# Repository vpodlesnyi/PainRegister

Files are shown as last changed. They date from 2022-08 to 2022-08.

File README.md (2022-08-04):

# PainRegister
The PCB of an electrostimulator for the study of the method of objective pain registration.

Technical specifications:
- input voltage supply 5V;
- booster scheme on the UC3843BD1013TR;
- USB-UART module;
- main MCU STM32F103C8T6TR.

demo image

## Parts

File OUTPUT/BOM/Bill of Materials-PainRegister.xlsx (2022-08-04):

Description | Part Number | Value | Voltage | Designator | Quantity
DC-DC step-up converter for 5/32-V to 5/35-V |  |  |  | A1 | 1
USB UART module |  |  |  | A2 | 1
Конденсатор | GRM216R71H103K | 0,01мк | 50B | C1 | 1
Конденсатор | GRM21BR71H104KA01L | 0,1мк | 50В | C2, C3, C5, C9, C19, C21, C38 | 7
Конденсатор | GRM21BR71H105K | 1мк | 50B | C4, C6, C37 | 3
Конденсатор полярный | TAJD336K035RNJ | 33мк | 35В | C7 | 1
Конденсатор полярный | 293D106X9016A2TE3 | 10мк | 16В | C8, C22, C24, C25, C26, C36 | 6
Конденсатор | GRM188R71H104KA93D | 0,1мк | 50B | C10, C11, C13, C14, C15, C16 | 6
Конденсатор | CC0603JRNPO9BN220 | 22 | 50B | C12, C17 | 2
Конденсатор | GRM31CR71E106KA12L* | 10мк | 25В | C18 | 1
Конденсатор | GRM21BR61E475KA12L | 4,7мк | 25B | C23, C33 | 2
Конденсатор | GRM32ER71H106K | 10мк | 50В | C27 | 1
Конденсатор | GRM1885C1H151J | 150 | 50B | C28 | 1
Конденсатор | GRM319R71H223K | 0,022мк | 50В | C29 | 1
Конденсатор полярный | ECAP33uF/450V | 33мк | 450В | C30 | 1
Конденсатор | GRM1885C1H101J | 100 | 50B | C31 | 1
Конденсатор | GRM216R71H222K | 2200 | 50В | C34 | 1
Конденсатор | CC1206JRNPOBBN101 | 100 | 500В | C35 | 1
Low Cost Low Power Instrumentation Amplifier | INA122PU |  |  | DA1 | 1
4-Bit Bidirectional Voltage-level Translator | TXB0104PWR |  |  | DA2 | 1
Step-Down DC-DC Converter | LM3671MF-3.3/NOPB |  |  | DA3 | 1
High and Low Side Driver | IR2110STRPBF |  |  | DA4 | 1
Current Mode PWM Controller for Forward and Flyback Applications | UC3843BD1013TR |  |  | DA5 | 1
Medium-density performance line ARM®-based 32-bit MCU with 64 or 128 KB Flash, USB, CAN, 7 timers, 2 ADCs, 9 com. interfaces | STM32F103C8T6TR |  |  | DD1 | 1
Предохранитель | MF-MSMF260 |  |  | FU1 | 1
EMI Suppression Filter | BLM18PG181SN1D | 0 |  | L1 | 1
EMI Suppression Filter | SRR0604-3R3ML | 3,3мкГн |  | L2, L4, L6, L8 | 4
EMI Suppression Filter | CM201212-R18KL | 0,18мкГн |  | L3, L5, L9 | 3
EMI Suppression Filter | SRP1770TA-101M | 100мкГн |  | L7 | 1
Резистор | RC0805FR-07100RL | 100 |  | R1 | 1
Potentiometer | 3296Y-1-202LF | 2к |  | R2 | 1
Резистор | RC0805FR-07510RL | 510 |  | R3 | 1
Резистор | RC0805FR-0747RL | 47 |  | R4, R21 | 2
Резистор | RC1206FR-074M3 | 4,3М |  | R5 | 1
Резистор | RC0805FR-071KL | 1к |  | R6, R19, R24 | 3
Резистор | RC0805FR-0710RL | 10 |  | R7, R26 | 2
Резистор | RC0805FR-0747KL | 47к |  | R8, R11, R25 | 3
Резистор | RC0603FR-0710KL | 10к |  | R9, R10 | 2
Резистор | RC1206FR-071M2 | 1,2М |  | R12 | 1
Резистор | RC0805FR-0710KL | 10к |  | R13, R23 | 2
Резистор | RC0805FR-070RL | 0 |  | R14, R15 | 2
Резистор | RC0805FR-077K5 | 7,5к |  | R16 | 1
Резистор | RC1206FR-07100RL | 100 |  | R17 | 1
Potentiometer | 3296Y-1-203LF | 20к |  | R18 | 1
Резистор | RC0805FR-07150RL | 150 |  | R20 | 1
Резистор | KNP-2W-1KJ | 1 |  | R22 | 1
Резистор | RC1206FR-07150RL | 150 |  | R27 | 1
Резистор | RC0805FR-0791RL | 91 |  | R28 | 1
Резистор | RC2512FR-07330RL | 330 |  | R29 | 1
Кнопка |  |  |  | S1 | 1
Диод | SMA4007 |  |  | VD1, VD8 | 2
Диод Шоттки | PMEG2010AEB.115 |  |  | VD2, VD7 | 2
Диод | GS1M |  |  | VD3 | 1
Cтабилитрон (лавинный выпрямительный диод) односторонний | SMAJ5.0A |  |  | VD4 | 1
Диод Шоттки | MBR0520LT1 |  |  | VD5, VD9 | 2
Диод Шоттки | SK34A |  |  | VD6 | 1
Светодиод | KP-2012EC |  |  | VD10, VD11 | 2
N-MOSFET | IRLML6401TRPBF |  |  | VT1 | 1
N-MOSFET | IRF840ASPBF |  |  | VT2, VT3, VT4 | 3
Разъем - 6 конт. вилка | DS1021-1*6SF112-B |  |  | X1 | 1
Разъем - 2 конт. розетка | DS1069-2 MR-A |  |  | X2 | 1
Разъем - 2 конт. клеммник |  |  |  | X3 | 1
Кварцевый резонатор | KX-9A |  |  | Z1 | 1

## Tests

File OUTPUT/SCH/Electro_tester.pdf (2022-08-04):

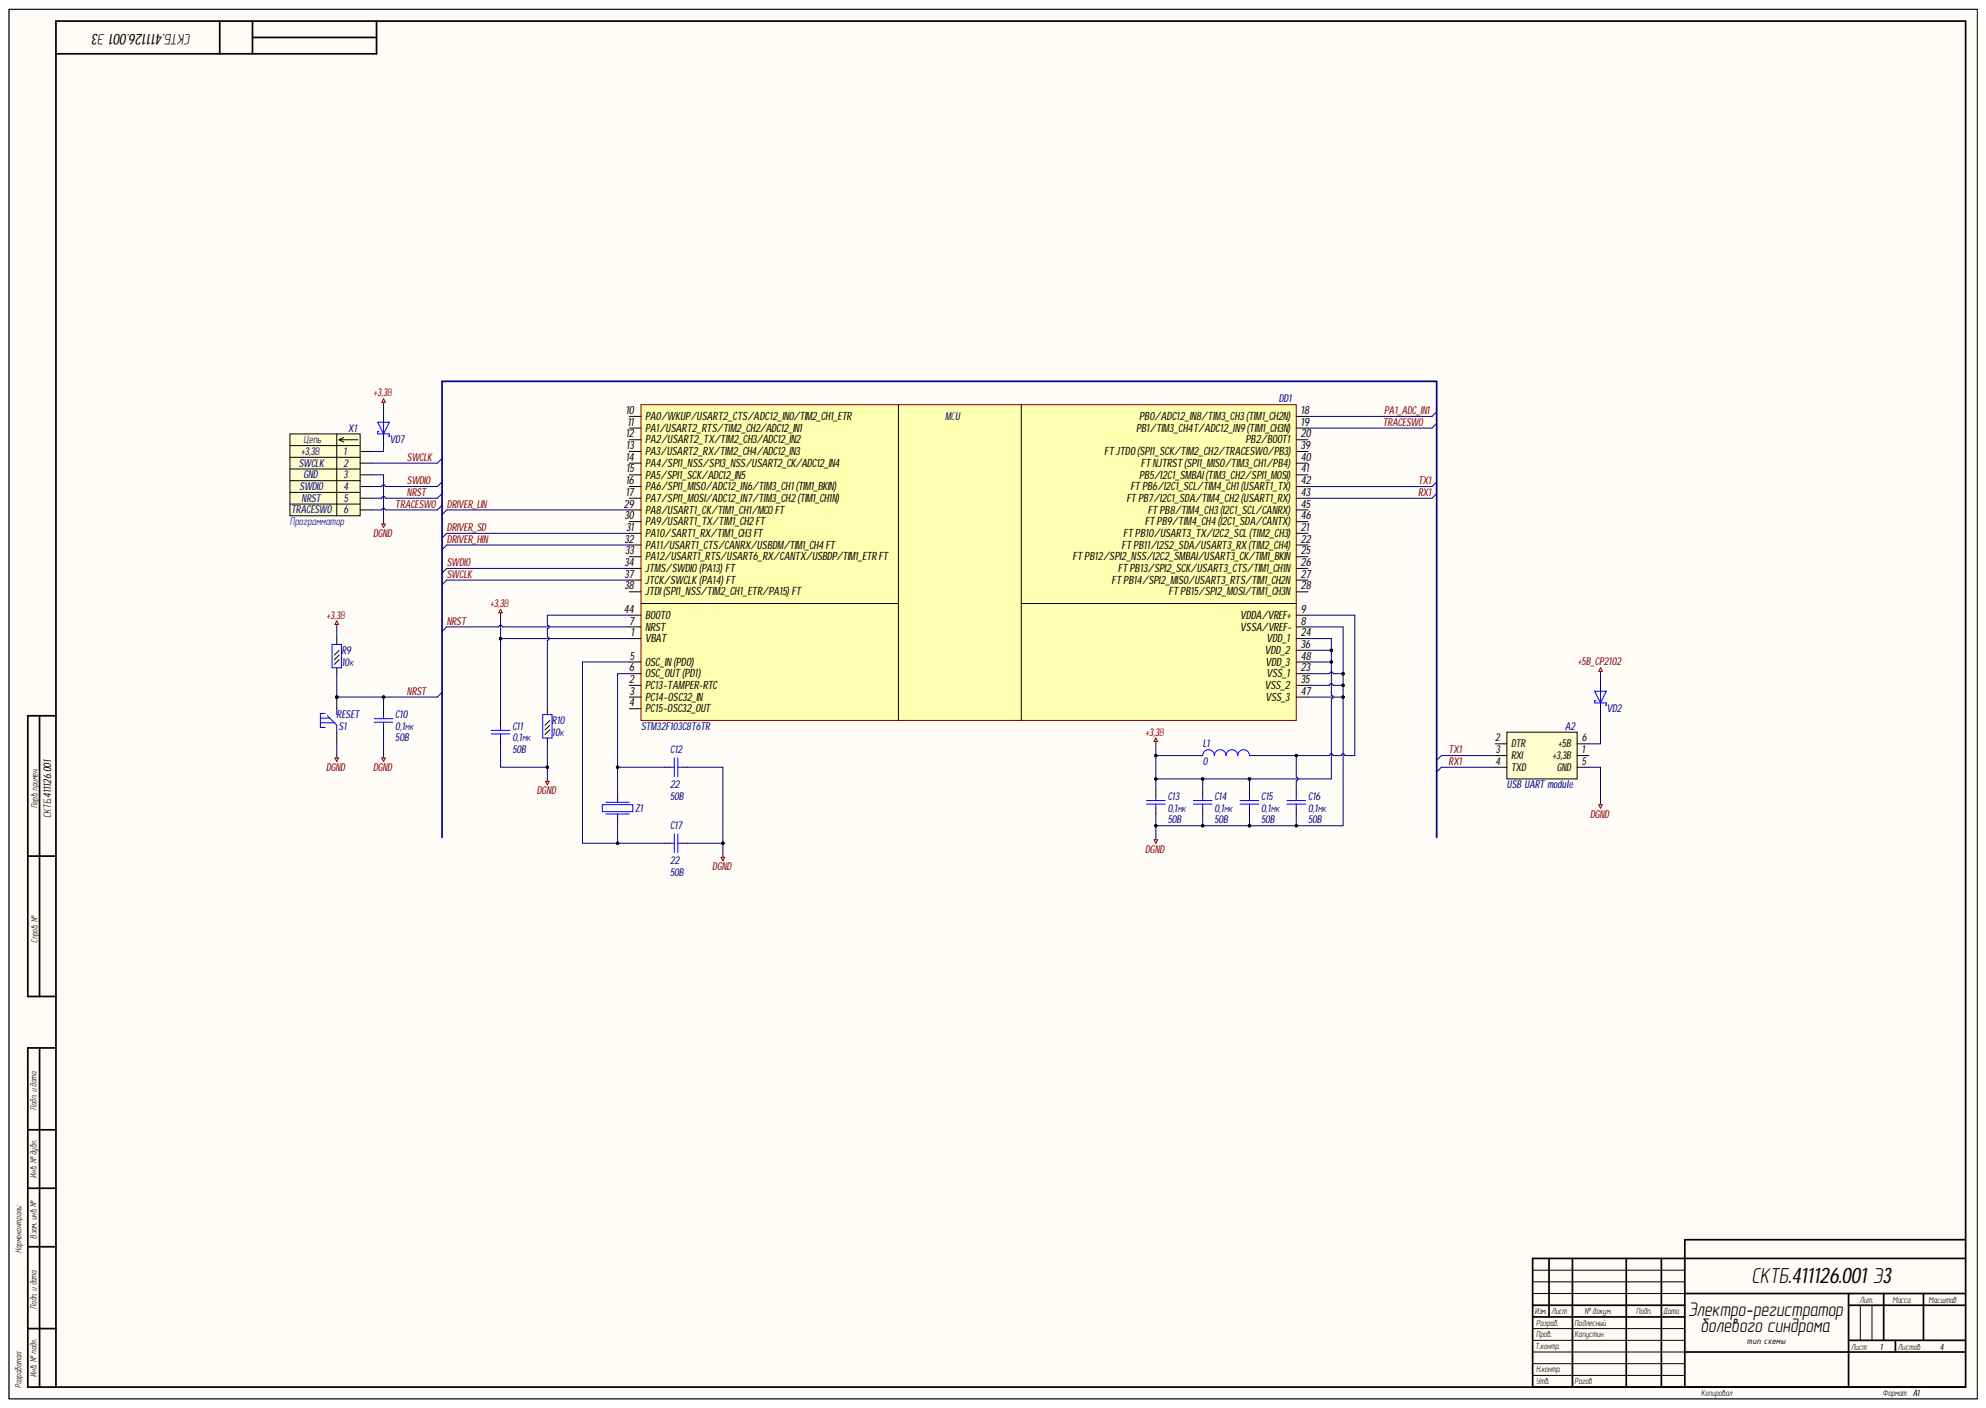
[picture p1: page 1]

PA0/WKUP/ USART2_CTS/ADC12_IN0/TIM2_CH1_ETR PA1/ USART2_RTS/TIM2_CH2/ADC12_IN1 PA2/ USART2_TX/TIM2_CH3/ADC12_IN2 PA3/ USART2_RX/TIM2_CH4/ADC12_IN3 PA4/ SPI1_NSS/ SPI3_NSS/ USART2_CK/ADC12_IN4 PA5/ SPI1_SCK/ADC12_IN5 PA6/ SPI1_MISO/ADC12_IN6/TIM3_CH1 (TIM1_BKIN) SPI1_MOSI/ADC12_IN7/TIM3_CH2 (TIM1_CH1N) PA7/ PA8/ USART1_CK/TIM1_CH1/ MCO FT PA9/ USART1_TX/TIM1_CH2 FT PA10/ SART1_RX/TIM1_CH3 FT PA11/ USART1_CTS/CANRX/ USBDM/TIM1_CH4 FT PA12/ USART1_RTS/ USART6_RX/CANTX/ USBDP/TIM1_ETR FT JTMS/ SWDIO (PA13) FT JTCK/ SWCLK (PA14) FT JTDI (SPI1_NSS/TIM2_CH1_ETR/ PA15) FT | MС U | PB0/ADC12_IN8/TIM3_CH3 (TIM1_CH2N) PB1/TIM3_CH4T/ADC12_IN9 (TIM1_CH3N) PB2/ BOOT1 FT JTDO (SPI1_SCK/TIM2_CH2/TRACESWO/ PB3) FT NJTRST (SPI1_MISO/TIM3_CH1/ PB4) PB5/I2C1_SMBAI (TIM3_CH2/ SPI1_MOSI) FT PB6/I2C1_SCL/TIM4_CH1 (USART1_TX) PB7/I2C1_SDA/TIM4_CH2 (USART1_RX) FT FT PB8/TIM4_CH3 (I2C1_SCL/CANRX) FT PB9/TIM4_CH4 (I2C1_SDA/CANTX) FT PB10/ USART3_TX/I2C2_SCL (TIM2_CH3) FT PB11/I2S2_SDA/ USART3_RX (TIM2_CH4) FT PB12/ SPI2_NSS/I2C2_SMBAI/ USART3_CK/TIM1_BKIN FT PB13/ SPI2_SCK/ USART3_CTS/TIM1_CH1N FT PB14/ SPI2_MISO/ USART3_RTS/TIM1_CH2N FT PB15/ SPI2_MOSI/TIM1_CH3N

DRIVER_HIN 32 | 22
33 SWDIO | 25

SWCLK 37 | 27

BOOT0 NRST STM32F103C8T6TR VBAT OSC_IN (PDO) OSC_OUT (PD1) PC13-TAMPER-RTC PC14-OSC32_IN PC15-OSC32_OUT | VSSA/VREF-VDD_1 VDD_2 VDD_3 VSS_1 VSS_2
1 | | 24
5 | | 36

Инв. № подл. Инв. № дубл. Подп. и дата Взам. инв. № Подп. и дата Перв. примен. Справ. №

СКТБ.411126.001 Э 3

болевого синдрома Электро-регистратор тип схемы | Лит . | Масса | Масш таб

Изм . | Лист | № докум . | Подп . | Дата
Разраб . | | Подлесный
Пров . | | Капуст ин
Т .кон тр . | | | | | Лист | Листов

Н .кон тр .
У тв. | Рого в

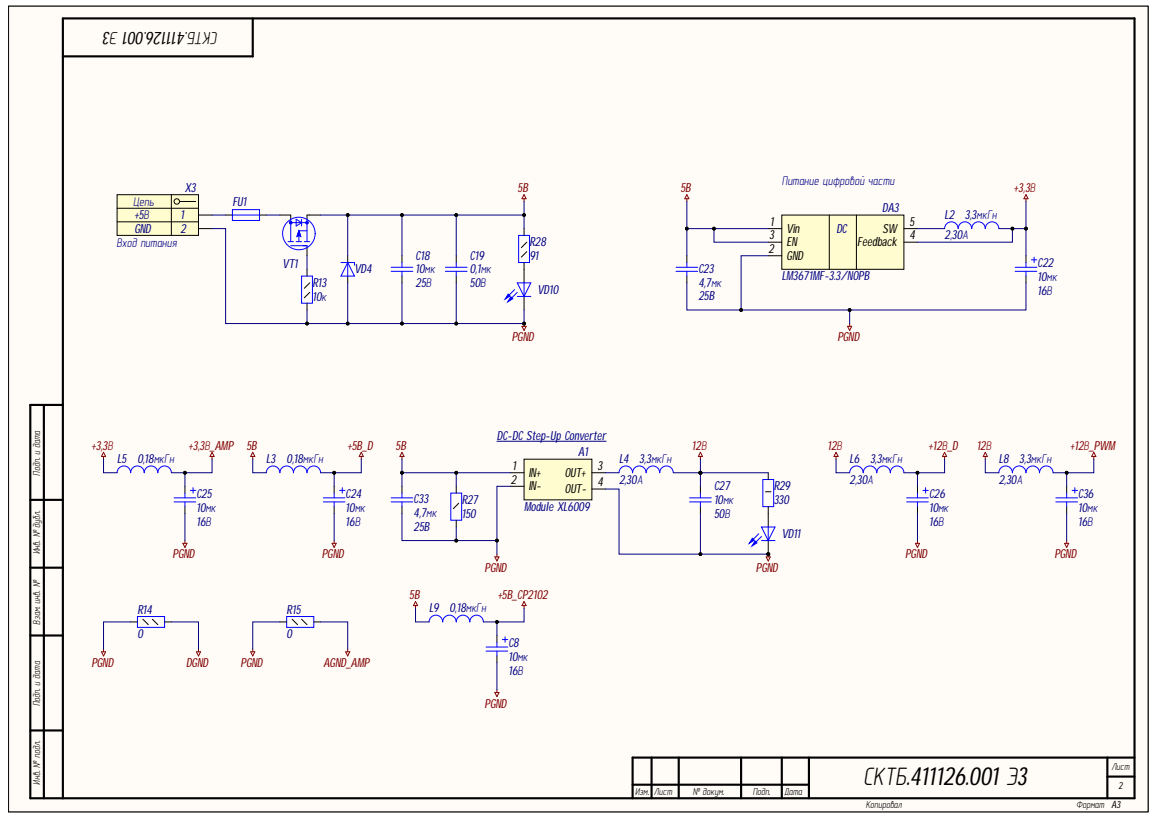
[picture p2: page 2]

+5В | 1
GND | 2

СКТБ.411126.001 Э3 в. № подл. Инв. № дубл. Подп. и дата Взам. инв. № Подп. и дата

DC-DC Step-Up Converter

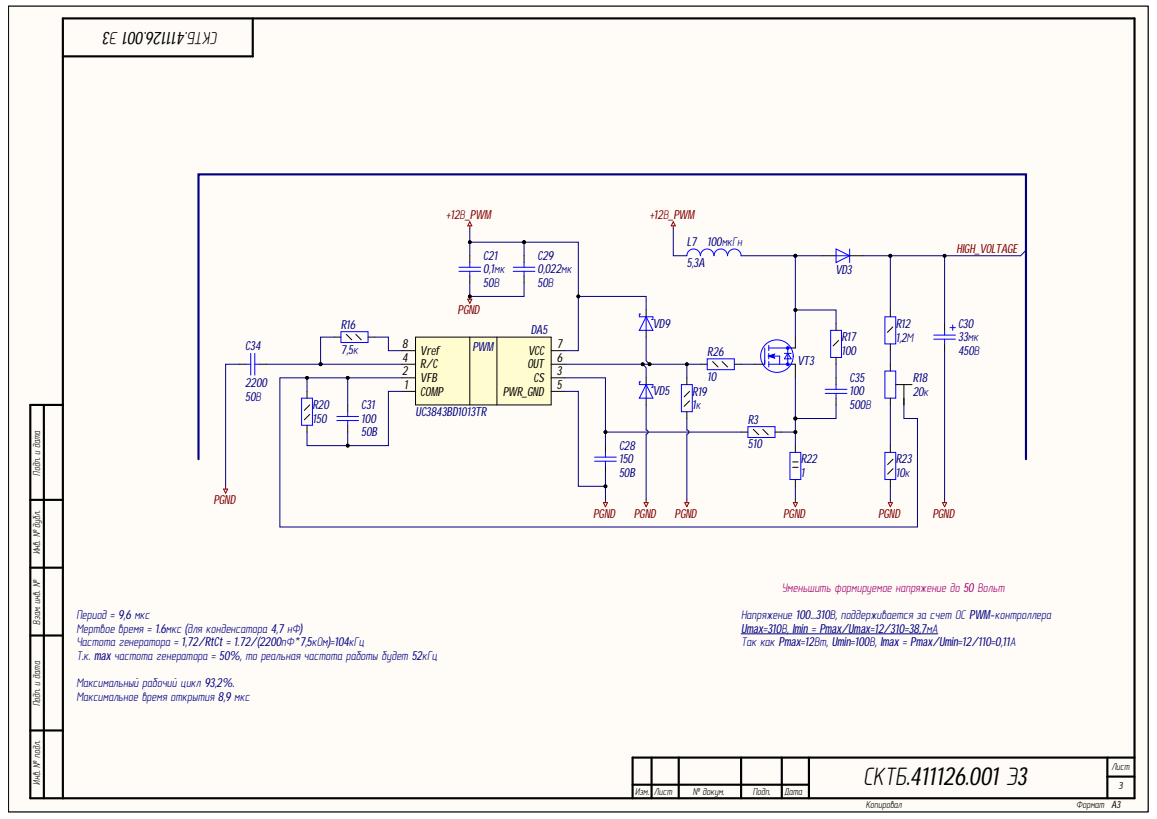
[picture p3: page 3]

в. № подл. Инв. № дубл. Подп. и дата Взам. инв. № Подп. и дата

Уменьшить формируемое напряжение до 50 Вольт

Период = 9,6 мкс
Мертвое время = 1.6мкс (для конденсатора 4,7 нФ) Т.к. max частота генератора = 50%, то реальная частота работы будет 52кГц

Напряжение 100...310В, поддерживается за счет ОС PWM-контроллера
Umax=310В, Imin = Pmax/Umax=12/310=38,7мА

Максимальный рабочий цикл 93,2%.
Максимальное время открытия 8,9 мкс

СКТБ.411126.001 Э | Лист3

. | Лист | . | Подп

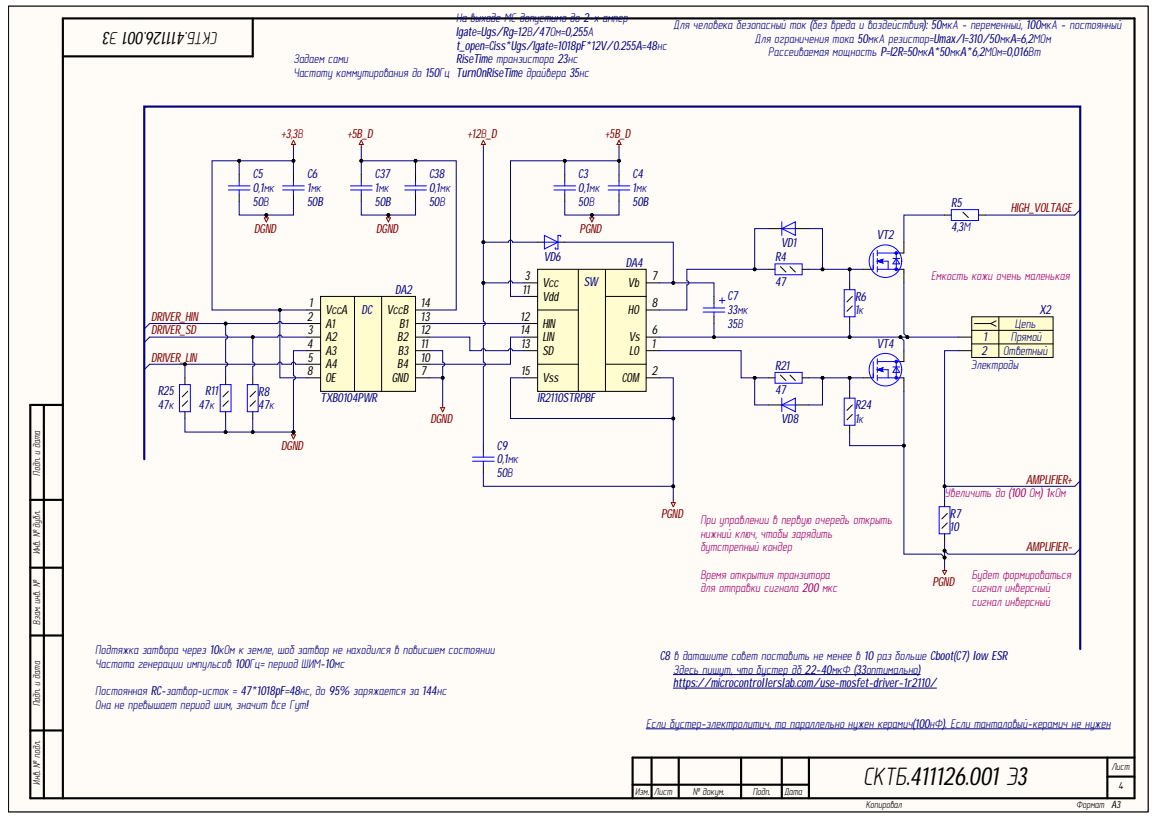
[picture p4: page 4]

На выходе МС допустимо до 2-х ампер
Igate=Ugs/Rg=12В/47Ом=0,255А
t_open=Ciss*Ugs/Igate=1018pF*12V/0.255A=48нс
RiseTime транзистора 23нс
TurnOnRiseTime драйвера 35нс

Для человека безопасный ток (без вреда

Для ограничения тока 50мкА резистор=Umax/I=310/50мкA=6,2МОм
Рассеиваемая мощность P=I2R=50мкA*50мкA*6,2МОм=0,016Вт

Vcc | | SW | Vb

Емкость кожи очень маленькая

Цепь

3 | LIN 14
4 | | | SD 13 | | 1
8 | | 0,1мк | | Vss 15 | COM

12 | Прямой
Ответный

в. № подл. Инв. № дубл. Подп. и дата Взам. инв. № Подп. и дата

При управлении
нижний ключ, чтобы зарядить
бутстрепный кондер

Время открытия транзитора
для отправки сигнала 200 мкс

Подтяжка затвора через 10кОм
Частота генерации импульсов 100Гц= период ШИМ-10мс

к земле, шоб затвор не находился

в даташите совет поставить не менее
Здесь пишут, что бустер дб 22-40мкФ (33оптимально)
https://microcontrollerslab.com/use-mosfet-driver-1r2110/

в 10 раз больше Cboot(C7) low ESR

Постоянная RC-затвор
Она не превышает период шим, значит все Гут

-исток = 47*1018pF=48нс, до 95% заряжается за 144нс

-электролитич, то параллельно нужен керамич(100нФ). Если танталовый

СКТБ.411126.001 Э | Лист4

. | Лист | . | Подп

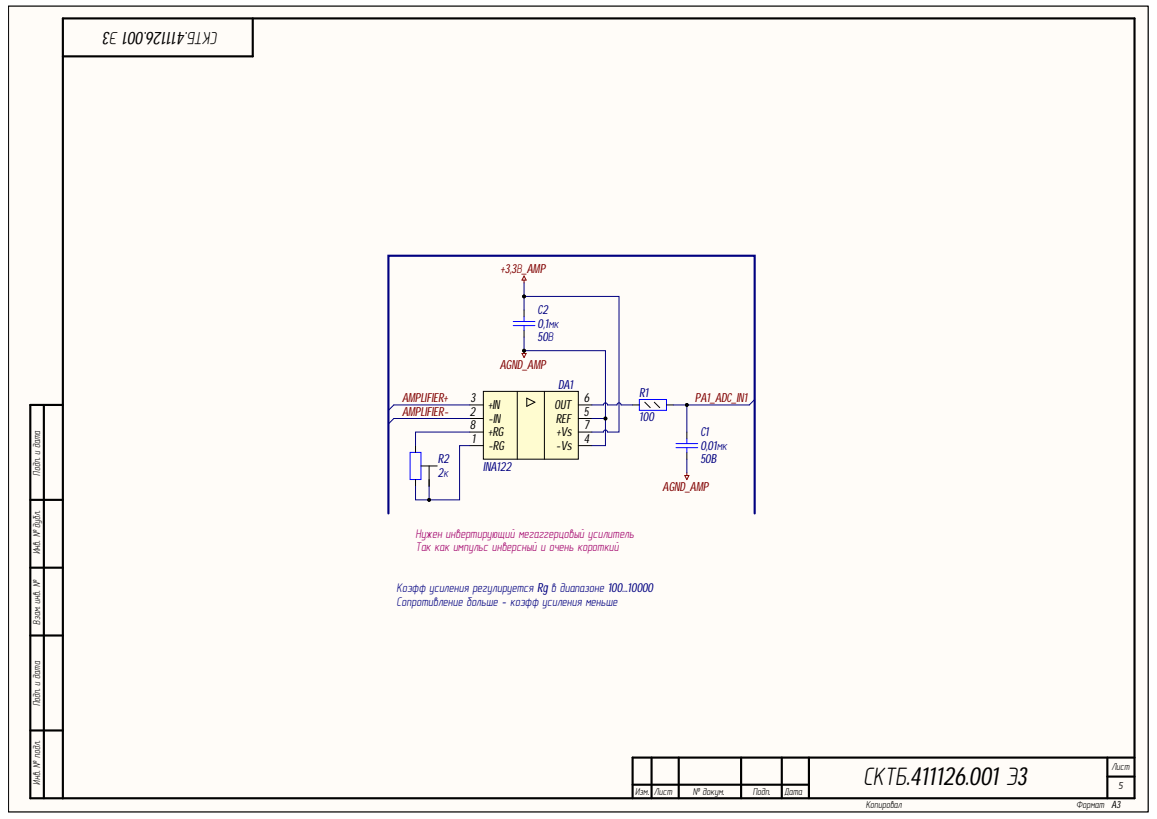
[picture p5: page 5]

СКТБ.411126.001 Э3 в. № подл. Инв. № дубл. Подп. и дата Взам. инв. № Подп. и дата

Нужен инвертирующий мегаггерцовый усилитель
Так как импульс инверсный и очень короткий

Коэфф усиления регулируется Rg в диапазоне 100...10000
Сопротивление больше - коэфф усиления меньше

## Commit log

2018-10-14 Первая попытка создания схемы обратноходовика
    [PainRegister.PrjPcb, PainRegister.SchDoc]
2018-10-14 Создал файл READ.me
2022-08-04 Reorganized documents.
    [Bill of Materials-PainRegister.xlsx, Booster_scheme_transformator.SchDoc, DENAS_Scheme.SchDoc, PainRegister.GBL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]
